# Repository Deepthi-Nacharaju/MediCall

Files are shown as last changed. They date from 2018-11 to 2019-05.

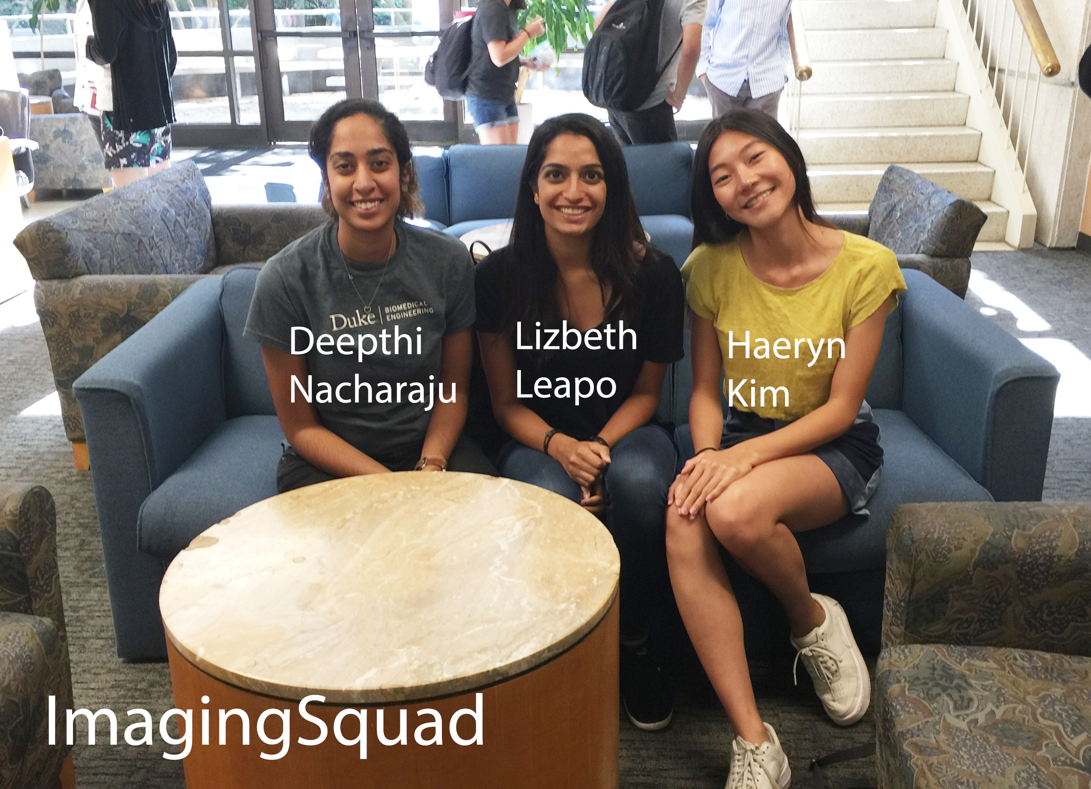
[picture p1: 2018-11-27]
Fall18/General/590TeamNames.jpg

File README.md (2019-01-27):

# MediCall

## Directory of Repository

| Subject                                 | Folder            | File Name                                                                      | Objectives      |
|-----------------------------------------|-------------------|--------------------------------------------------------------------------------|-----------------|
| Project Organization Strategies         | General           | ProjectOrganization.pdf                                                        |                 |
| Old Design Foundations Document         | Cycle_One         | 10_11_18 Design Foundations Document (DFD).docx                                |                 |
| Medical Device Development Worksheet    | Cycle_One         | HaerynLizDeepthi_Medical Device Development Worksheet 2018.xlsx                |                 |
| Updated Design Foundation Document      | Cycle_Two         | Updated Design Foundations Document (DFD).pdf                                                               |                 |
| Updated Spec Sheet PDF                  | Cycle_Two         | HOQ and Specs.pdf                                                              |                 |
| Cycle 2 Presentation                    | Presentations     | Final_Presentation.pptx                                                        |                 |
| Functional Decompositions               | Cycle_Two         | FunctionalDecomposition.pdf                                                    | Objective 1     |
| Pugh Matrix for Patient Alert Mechanism | Cycle_Two         | Scoring_User_Alert.xlsx                                                        | Objective 2     |
| Pugh Matrix for Nurse Alert Mechanism   | Cycle_Two         | Scoring_Alert.xlsx                                                             | Objective 3     |
| Pugh Matrix for Sensing Mechanism       | Cycle_Two         | Scoring_Sensor.xlsx                                                            | Objective 4     |
| +/- List for Battery v. Wall Power      | Cycle_Two         | BatteryvsMains.xlsx                                                            | Objective 5     |
| Pugh Matrix for Battery Type            | Cycle_Two         | Scoring_Battery.xlsx                                                           |                 |
| Hospital Policy on Bluetooth and Wifi   | Cycle_Two         | Bluetooth vs. Wifi Regulation Research.pdf                                     | Objective 6     |
| Sketch of System                        | Cycle_Two         | sketchofsystem.pdf                                                             | Objective 7     |
| Mechanical CAD of System                | Mechanical        | sensor.SLDPRT; sensor holder.SLDPRT; clamp.SLDPRT; strokesensorassembly.SLDASM | Objective 7     |
| Software Code Block Diagram             | Cycle_Two         | codeblockdiagram.pdf                                                           | Objective 8     |
| Demo Video of Prototype                 | Data              | IMG_7550.MOV                                                                   | Objective 9, 10 |
| List of System Components               | General           | Materials .xlsx                                                                |                 |
| Patient Flow Chart                      | Problem Statement | Patient flow-chart.pdf                                                         |                 |
|Updated Design Foundations Documentation| Cycle_Two| Updated Design Foundations Documentation. pdf

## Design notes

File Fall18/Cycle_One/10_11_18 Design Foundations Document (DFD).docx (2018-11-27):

MediCall: Design Foundations Document (DFD)

__________________________

Deepthi Nacharaju, Lizbeth Leapo, Haeryn Kim

Section 1: Design Context Review

In the United States alone, there are almost 36 million inpatient hospitalizations per year¹ with an average stay of 4.5 days². Many conditions can account for this staggering number of days spent in the hospital. The most common reason for this hospitalization is pregnancy, or neonatal in nature¹. In the ages of 65+, these reasons include heart disease, osteoarthritis, and back problems, the latter two of which can have a large impact on a patient’s mobility¹. As Americans spend increasingly large periods of time in hospitals, there should be an effort to make these stays as comfortable as possible.

During a time that can be scary, isolating, and stressful, people look to others for support and company. Though hospitals generally have visiting hours for family and friends to come see a patient, people often find themselves alone in their rooms. While patients are in inpatient care, they frequently need to call a nurse for help to use the restroom, eat, shift in their bed, and ask for medication. Rooms are usually set up with a call system, that can include a call bell, that enables the patient to alert their caregivers that help is needed. Beyond this, accessibility to reliable and efficient call bells reduces anxiety in the patient and increases family satisfaction with the stay³. Families are much more at ease leaving their loved ones in the hospital when they know a nurse is available nearby. Quick response times have even been shown to reduce fall risk and the incidence of pressure ulcers³. Nurses can help patients move from their bed to a chair and even the bathroom. Patients are also able to alert someone when they are uncomfortable from lying in the same position for too long. These are all important reasons why this line of communication is vital to a patient’s well-being.

There exist statewide regulations for the requirement of call bell or communication systems at nursing stations. For example, North Carolina has the following extensive requirement:

“In general patient areas, each room shall be served by at least one calling station and each bed shall be provided with a call button[...] Calls shall register with the floor staff and shall activate a visible signal in the corridor at the patient's or resident's door[...]A nurses' call emergency button shall be provided for patients' and residents' use at each patient and resident toilet, bath, and shower”⁴

The regulations go on to outline the number of call buttons required in rooms with multiple beds or bed stations, and even light indicators at corridor intersections. Other states, such as the state of Michigan, has no regulations regarding physical parameters of nursing stations⁴. In order for a solution to have potential market applications in the entire country, it must meet the most stringent of regulations, and in this case, encompass indicator lights and emergency buttons as well.

One study found the average number of calls placed by a patient to the nursing station to be 12 per day, with an increase in frequency around meal times⁵, perhaps to request help with trips to the restroom, or to ask for more food. Multiplying this value with the number of patients in a given unit – nurses receive 100 calls a day. With this high rate, the call bell must be reliable while also not cluttering the to-do list of nurses. A common complaint of the nurses in the study was that the high frequency of calls was disruptive to their busy shifts. Assessments, treatments, and teaching were now littered with patient calls⁵. There is a delicate balance between addressing immediate patient needs and tending to a longer term treatment plan composed of blood tests and imaging orders. Despite this, average response time was just 11 seconds⁵. This demonstrates that competing communication systems should be extremely efficient in transferring patient input, but also not be overly confusing, obtrusive, or disordered.

Current technologies include touch screens, hand held remotes, and pancake sensors for patients to create a user input. This signal is then translated to either a centralized screen at the nurses station, or a particular medical personnel’s handheld device³. Some systems even include a verbal system in which the patient indicates their specific need, and the receiver determines if the call should be routed to a registered nurse or to a nurse’s assistant⁴. Instead of just a generic call bell, some systems also indicate the specific need, and allow the user to choose from several common call requests. The patient lets the nurse know they need to use the restroom, change the channel, or shift their position remotely. What these systems typically seem to lack is feedback from the unit to the user that the call mechanism has been triggered. Because alertness or cognition in these patients, especially neurological patients, can be diminished, this feedback is vital to ensure that a purposeful call has been triggered or than an accidental one has not been placed. On the other hand, some sensors are too easily triggered, calling for nurses when the patient was merely shifting in their bed. This leads to further frustration, and nurses and patients often throw the call system aside altogether.

Physical sensors like these are often limited to use by patients with full mobility and dexterity in their hands. The systems that require verbal input are limited to those who can speak loudly and clearly. Finding a suitable system for patient populations with limited speech or physical capabilities remains a challenge.

Patients in the Neurocritical Care Unit of the Duke Medicine Pavilion, or DMP, suffer from a wide range of ailments that vary in severity and also vary the length of each stay. Frequently, patients have suffered from strokes, resulting in paralysis that ranges from monoplegia to quadriplegia⁶. Some patients have considerable dexterity in their upper extremities, while others are completely paralyzed and can barely speak or see. Loss of function in the arms and legs can be especially dangerous because the patient is not able to catch his or her falls, rotate to ease pain from lying on their backs for long periods of time, or move to the restroom. Paralysis can also result from other neurological diseases, including physical trauma, neuropathy, and Parkinson’s Disease. The loss of any important functions limits accessibility to remotes with several buttons, or verbal cues.

Similar limitations can be found in other clinical populations, including young people suffering from orthopedic injury, and middle-aged patients battling cancer. This creates a larger context for the relevance of this issue. Outside of neurological units, loss of motor skills can be prevalent in oncology, trauma, and cardiac centers across the country. Any patient that is admitted to the hospital, could potentially find him or herself too weak or entirely unable to lift their arms, while simultaneously at need of frequent attention and care. In any combination, these limitations can be extremely detrimental in calling for help and could result in increased risk of death or serious injury.

At the Duke Medicine Pavilion, there are several adapted call bells in place, three of which are pictured below in Figure 1⁷. These include the standard call bell with a button on the patient’s TV remote, a handheld push-button call bell, and a pancake call bell. The push-button and pancake call bell are used for patients with a larger degree of physical or cognitive impairment.

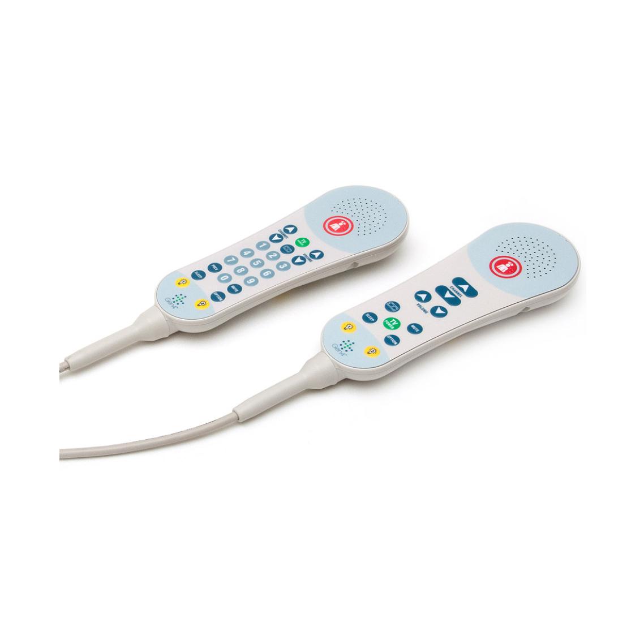
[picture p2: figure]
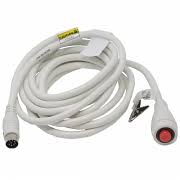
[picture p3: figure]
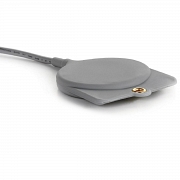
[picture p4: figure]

Figure 1. Call bells implemented in the Duke Medicine Pavilion. From left to right, the standard TV remote call bell, the handheld push-button call bell, and the pancake call bell¹³.

After observing the use of these devices in the Neurocritical Care Unit of the DMP, it became evident that while there are adapted call bells for patients with specific physical or cognitive needs, several factors still result in faulty patient-to-nurse communication. The standard call bell is designed for patients with very few physical or cognitive limitations. However, this bell is also often provided to patients with visual impairments who struggle to differentiate the call bell button from the TV remote buttons. Nurses sometimes attach ECG leads to the call bell button on the remote to make it easier for those patients to use the call bell function. The push-button call bell works well for patients with a relatively high degree of hand dexterity, but the button has no stand, and often gets dropped on the floor or lost in the hospital bedding. The button also has no feedback mechanism to alert the patient that it has been activated. This generally leads to a high number of false pages to the nurses’ station. The pancake sensor has a similar problem. It is designed for patients with very limited hand dexterity. However, it is extremely sensitive and does not have a feedback mechanism. According to Kim Powell, a speech pathologist who works in the Neurocritical Care Unit, the pancake sensor is far too sensitive to be used effectively and it results in the largest amount of false alerts.

Each call bell in a patient room, regardless of the type of call bell, is connected first to a station on the patient’s ECG cart, and then to a wall power supply. One of the largest failures of the call bell system at the DMP is the lack of attention in plugging in both of these connections. This also dramatically reduces patients’ accessibility to nurses when in need.

It is critical that patients are able to contact nurses when they are in need of assistance. Patients with limited hand dexterity find both standard and adapted call bells at Duke to be particularly unhelpful. The systems are either physically inaccessible, unplugged, or too sensitive. The ultimate challenge is addressing all of these inconveniences with one device or system.

Our primary need is to find a way to address inadequate patient-to-nurse communication in patients with limited hand mobility that increases accessibility to nurse assistance while reducing the number of false alerts caused by current call bell systems.

Section 2: Market Analysis

In the context of this problem, there were two ways to segment the available market. The first was according to medical unit or service provider the patient would seek out to receive care. The market includes smaller segments such as palliative care units, surgical in-patient clinics, and at home care.

The target segments of focus include Nursing and Retirement homes with a predicted total addressable market (TAM) of $42,228,000⁸,⁹ and Neurocritical Care Units (NCUs) with a TAM of $262,800¹⁰,¹¹. The primary criteria used to determine the target segment includes a target population that experiences limited mobility of their upper extremities, with potential limitations in speech, sight, and cognition.

Care systems for the elderly regularly take care of people at the end of their life. In this stage, people experience declines in both physical and mental health, demonstrated by decreases in balance, dexterity, muscle strength, and mental sharpness. These people would also experience potential challenges with using traditional call bell systems. In the United States, the entire population of nursing and retirement homes includes 15,600 Nursing homes with 1.7 million beds⁹. This translates to about 109 beds per facility and a need for an equivalent number of call bells. In order to determine their willingness to pay, competitive products were analyzed for cost per unit.

Competitive products can be found in Table 1, below. Each system was broken down into per patient room costs. For example, a system that cost $1,000, but supplied 10 individual modules, was translated to a $100/bed cost. On average, the cost per bed was $150. To calculate predicted Total Addressable Market (TAM), the number of estimate beds per segment in the US was multiplied by the cost per bed. For the Nursing/Retirement home segment, there are estimated number of 15,640 homes with an average of 108 beds. The total of 1,689,120 beds was multiplied by $150/bed for a TAM of $42,228,000⁸,⁹.

NCUs also care for a patient population with physical and mental limitations. NCUs typically treat acute ischemic strokes, cases of meningitis, traumatic brain injury and cerebral aneurysms, along with a host of other potentially fatal conditions. Patients experience varying levels of consciousness and frequently need to alert a nurse when they are awake. However, with this level of brain injury, many patients experience spastic or disjointed movements of their extremities. Across the country there are 73 of these units¹⁰. Similar conditions can be also found in Neurology units, which are found more frequently in hospitals. Estimating the number of beds per unit to be around 24, coming from the number of beds in Duke University’s Neurological ICU⁹, to total number of beds in the US as 1,752. Again, multiplying cost per bed equates to $262,800¹⁰,¹¹.

To further narrow down the target population, these segments were refined by considering the physiological limitations of the patients. This is the second way in which this market could be segmented. In general, there are three overarching themes to what created challenges while trying to utilize the traditional call-bell system, both in the larger scope of disabilities and in the Duke Medical Pavilion Neuro ICU client. These themes include cognitive impairments, when the patient lacks awareness or alertness to understand how a traditional button system works. The patients could also experience sensory loss, in which blindness prevents them from seeing the difference between various buttons on a remote. Another limitation is more physical in nature, where either paralysis or jerky movements have trouble exhibiting the dexterity needed for traditional call-bell systems.

After thorough market analysis, the primary target market segment will be those experiencing challenges with the mobility of upper extremities in Nursing/Retirement homes and Neurocritical Care Units, with potential for extension into other segments given success with this group.

Section 3: Identifying Customer Needs

Kim Powell is a clinical expert at the cross section of healthcare and communication, and a speech pathologist in the Neuroscience Department at Duke Hospital. She specializes in stroke recovery, and many of the devices in her unit are tailored to patients with limited hand dexterity, poor cognitive ability, or paralysis. Ms. Powell expressed the limitations of the sensitive adaptive devices such as the push-button and pancake call bells. She conveyed frustration with the wiring of the current call bell system and facilitated an introduction to a stroke patient who provided insight into image comprehension limitations post-stroke.

Observations during the shadowing visit led to the conclusion that the call-bells in the unit were either too sensitive and sent false alerts to nurses, or that they were entirely unused because they were either unplugged or physically inaccessible to the patient. There was a need to reduce the amount of excessive wiring attached to the call bell, so that it was accessible when needed, but not in the way otherwise. Patients with cognitive limitations also need a clear indication that the call-bell is activated, because the current devices do not provide any mode of feedback. The full list of customer needs is provided in Table 1 below.

Table 1. Identified Customer Needs

No. | Type of Need | Need | Priority
1 | Patient | Device is easily accessible for patients with limited hand dexterity | 1
2 | Patient | Device provides some mode of feedback when activated | 2
3 | Patient | Device will not be in the way when not in use | 3
4 | Nurse | Device transmits the signal to multiple receivers | 2
5 | Nurse | Device quickly transmits the signal to nurses | 2
6 | Nurse | Device reduces the amount of false alerts going to the nurses' station | 2
7 | Nurse | Device is durable and can withstand accidents | 5
8 | Nurse | Device reduces excessive wiring | 2
9 | Payer | Device has similar cost to other competitive nurse call systems | 4
10 | Payer | Device can be produced and purchased in bulk so hospitals can use in each patient room | 5
11 | Regulatory | Device complies with nursing units regulations set by NC | 2
12 | Regulatory | Device does not cause any adverse health effects, or pose a trip or fall hazard to the patients | 3
13 | Regulatory | Software on the device should meet IEC Medical Device Software Standards | 5

The customer needs are organized into patient needs, nurse needs, payer needs, and regulatory needs. This device has two primary users: the patient and the nurse. The patient needs deal with accessibility and use of device, while the nurse needs deal with the transmission and reliability of the alert in itself. The payer, Duke Hospital, needs this device to have a similar cost to competitive call systems. In terms of regulatory standards, the call system must comply with software and safety regulations met by the Duke Medicine Pavilion.

In establishing a hierarchy for our customer needs, increasing patients’ accessibility to nurses is a higher priority than reducing the amount of false alerts sent to nurses. The risk of a patient unable to get medical attention supersedes the inconvenience of a false alert. It is also important that the device provides some sort of feedback, which allows for easier use by patients with cognitive limitations, and subsequently reduces the amount of false alerts because it prevents repetitive pushing. Meeting state regulations for nursing units is also critical to ensure potential usage of our device in hospital rooms. Long-range and fast signal transmission was prioritized over durability, because an effective and fast alert is most beneficial to the patient and nurse. Reducing the amount of wires is a medium priority, because it is more of an inconvenience than a significant risk. Cost-efficiency and meeting software standards were of lowest priority because we first want to establish an effective and reliable device.

Section 4: Design Specifications

In order to reliably quantify the accuracy with which our product serves the customer needs, the following design specifications were determined to serve as quantitative judgment criteria.

Table 2. Target Specifications

Spec. No. | Need Nos. | Specification | Units | Competitive Value | Marginal Value | Ideal Value
1 | 3, 8, 12 | Wires from device to power | Number | 1-2 | 1 | 0 (wireless)
2 | 1, 2, 11 | Modes of button feedback (buzzing/light/sound) | List | 0 | 2 | 3
3 | 4 | Signal transmission range | m | 150 | 200 | 300
4 | 8 | Battery life | months | 0 (connected to wall power) | 2-3 | 6
5 | 7 | Water resistance | Standard | IPX5 | IPX4 | IPX5
6 | 1 | Weight of device | g | 110 | 100 | 50
7 | 9, 10 | Cost of device | $ | 150 | 100 | 70

The units include simple tallies (denoted as ‘numbers’), statistical values obtained through trials (in percentage), and categorization by standards. Standard pertains specifically to the requirements for water resistant devices as defined by the IP code, provided in the International Electrotechnical Commission (IEC) standard 60529¹². Whereas the search for comparable products did not provide their IP levels, we could narrow down the desired liquid ingress protection for our product. IPX5 means the device would be protected from a low level stream of water at any angle¹².

These criteria were determined by brainstorming the metrics associated with specific customer needs.To ensure that patients or nurses can easily access our product we wanted to make sure that it was easy to find and within reach, which is measured by the time it takes to find and activate the device. Current technologies at the DMP currently do not have feedback mechanisms, so a quantitative measure of types of feedback such as vibration, light, and sound was added as a specification. This specification also addresses the state regulation requiring a visible signal for nursing call units⁴. To address excessive wiring, the number of connections the device has to a wall plug or a source of power is a major specification. Some specifications were necessary to cover the basic functions of a call bell such as notifying the nurses within a reasonable range. The only customer need that was not matched by these quantitative specifications was the software regulation need (13), because this would require a qualitative check of the software.

Furthermore, we researched comparable products on the market and their design specifications to complement our specifications, as well as competitive values. For instance, the competitive value of cost was an averaged price projected on the nurse call products catalog of healthcare facilities companies¹³. Competitive values of weight were similarly found from comparable call bell products detailed in the market analysis. Competitive values for false alert rates were found in literature on alarm fatigue¹⁴. Ideal values were subjectively determined as the best possible values, without considering any scope or limitations of the project. Marginal values were determined as mid-range values between the competitive and ideal. For instance, whereas most systems were comprised of a base station dependent on wall plugs and pagers running on batteries with more than 6 months of battery life, 2-3 months of peak operation time were deemed as reasonable for our standalone, wireless communication device. Ideally, the device would be wireless with long battery life, water resistant, cheap, accessible in less than a minute, and have multiple modes of feedback.

Citations

[1] McDermott, K. W., Elixhauser, A., & Sun, R. (2017). Trends in Hospital Inpatient Stays in the United States, 2005-2014. Healthcare Cost and Utilization Project. https://www.hcup-us.ahrq.gov/reports/statbriefs/sb225-Inpatient-US-Stays-Trends.jsp

[2] Weiss, A. J., & Elixhauser, A. (2014). Overview of Hospital Stays in the United States, 2012. From Healthcare Cost and Utilization Project. https://www.hcup-us.ahrq.gov/reports/statbriefs/sb180-Hospitalizations-United-States-2012.pdf

[3] Galinato, J., Montie, M., Patak, L., & Titler, M. (2015). Perspectives of Nurses and Patients on Call Light Technology. Computers, Informatics, Nursing : CIN, 33(8), 359–367. http://doi.org/10.1097/CIN.0000000000000177

[4] Statewide Regulations for Nursing Units. (2011). Health Policy and Management. http://www.hpm.umn.edu/nhregsplus/NH%20Regs%20by%20Topic/NH%20Regs%20Topic%20Pdfs/PE%20-%20Nursing%20Unit/category_pe_nursing%20unit%20state%20regulations.pdf

[5] Roszell, S., Cheryl B. Jones, & Lynn, M. R. (2009). Call Bell Requests, Call Bell Response Time, and Patient Satisfaction. Journal of Nursing Care Quality, 24(1), 69-75. doi:10.1097/01.NCQ.0000342938.99036.9f

[6] Divani, A. A., Majidi, S., & Barrett, A. M. (2011). Consequences of Stroke in Community-Dwelling Elderly: The Health and Retirement Study 1998-2008. Stroke., 42(7), 1821-1825. doi:10.1161/STROKEAHA.110.607630

[7] Nurse Call. Medline. Retrieved from https://www.medline.com/category/Nurse-Call/Z05-CA15_12_02_07

[8] Smart Caregiver Two Call Buttons & Wireless Caregiver Pager. https://www.amazon.com/Smart-Caregiver-Buttons-Wireless-Pager/dp/B0032FMSWS

[9] Nursing Home Care. (2014). From Centers of Disease Control and Prevention. https://www.cdc.gov/nchs/fastats/nursing-home-care.htm

[10] Ward, M., Shutter, L., Branas, C., Adeoye, O., & Carr, B. (2012). Geographic access to US Neurocritical Care Units registered with the Neurocritical Care Society. Neurocritical Care, 16(2), 232-240. doi:10.1007/s12028-011-9644-2.

[11] Neurocritical Care Unit, Duke Medical Pavilion, 8E. Department of Neurology- Duke University School of Medicine. https://neurology.duke.edu/divisions/critical-care-and-vascular-neurology/neurocritical-care-unit-duke-medical-pavilion-8e

[12] International Electrotechnical Commission. (2013). Degrees of protection provided by enclosures (IP Code) (Standard No. 60529). Retrieved from https://subscriptions.techstreet.com/products/653435

[13] Curbell Medical. (2017). ‘Nurse Call and Healthcare Bed Accessories.’ Retrieved from https://curbellmedical.com/wp-content/uploads/pdfs/nurse_call/map466d_curbell_nurse_call_and_bed_products_catalog.pdf

[14] Jones, K. (2014). Alarm fatigue a top patient safety hazard. CMAJ- JAMC, 186(3), 178. doi: 10.1503/cmaj.109-4696

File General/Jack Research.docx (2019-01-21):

http://www.circuitbasics.com/how-to-hack-a-headphone-jack/

standard ¼” phone plug for single push button ^

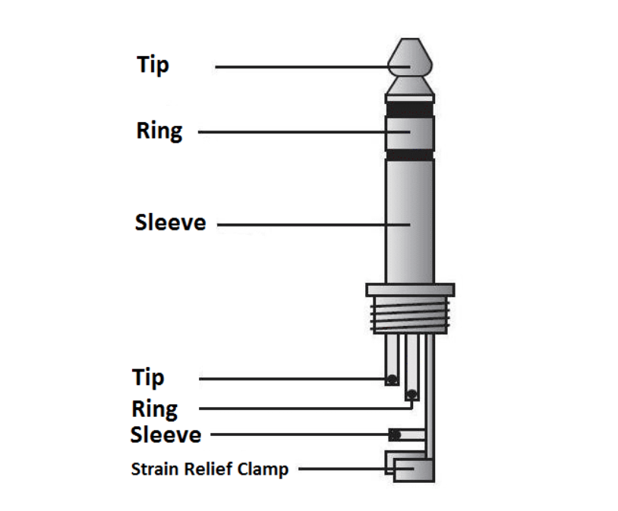
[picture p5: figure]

Tip = Power

Ring = Signal

Sleeve = Ground

1/21/19

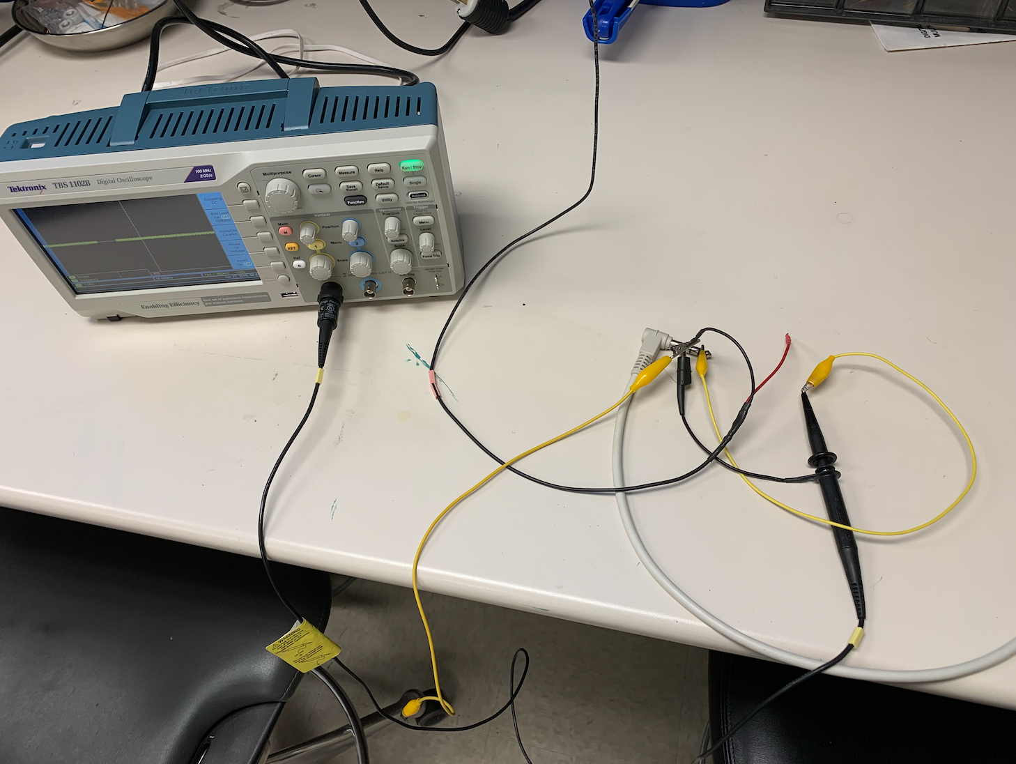
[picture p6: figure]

Deepthi: Used oscilloscope to probe both tip and ring with power on the other (5V). Saw signal when pushing the button but the power supply was maxing out a 1.5A. When power was on the ring, power supply was constantly maxed out; when power was on the tip, the power supply dropped down to 0A until the button was pushed (then it maxed out). Does the external circuit need a current limiting resistor….?

Further Questions:

Do we need to current limit the incoming signal?

How high and for how long does the voltage signal need to read high to trigger the wall system?

How does the nurse shut off the call?

What is the lag time between pushes for separate calls?

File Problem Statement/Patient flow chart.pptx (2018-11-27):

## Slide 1

Evidence of patella fracture? i.e. X-ray

Ambulatory care: initial diagnosis, treatment, rehabilitation

Patient has acute pain in the knee, and difficulty walking i.e. unable to lift foot

Displaced bones?

No

Apply cast or splint.

Closed fracture?

Have abrasions healed?

Surgical procedure

Pain management and rehab

No

No

Open fracture?

Ambulatory care: follow-up care

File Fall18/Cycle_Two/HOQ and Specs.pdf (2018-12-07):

### House of Quality, Functional Specs

Spec #1 | Spec #2 | Spec #3 | Spec #4 | Spec #5 | Spec #6 | Spec #7

Priority

CUSTOMER REQUIREMENTS/NEEDS

Time it takes to find and | Percentage of false positives | Number of connections from device to power | Number of different settings/ modes to adapt to varying hand dexterities | Battery life | Water resistance | Cost of device
1 | Easily accessible for patients with limited mobility | X | | | X
2 | Should be understood by patients with limited cognitive ability | | | | X
3 | Reduce the amount of false-positives going to the nurse's station | | X
4 | Reduces excessive wiring | | | X | | X
5 | Transmit the signal to multiple receivers
6 | Durable and can withstand accidents (ex. water spray) | | | | | | X
7 | Able to be produced/purchased at competitve cost | | | | | | | X
| | 1-2 min (2) | 85% (1) | 1-2 (Current system at Duke requires two connections to wall reach wall power) | 1 (per adapted call bell device) (3) | 0- Needs wall-power | IPX5 | $150 (from comparative chart on Market Analysis tab)

Competive Values
Marginal Value | 1 min | 20% | 1 | 2 | 2-3 months | IPX4 | $100
Ideal Value | 0.5 min | 5% | 0- wireless | 4 (one device for various types of mobility) | 6 months | IPX5 | $70

Sources:
1. https://www.ncbi.nlm.nih.gov/pmc/articles/PMC3928208/
2. https://www.frequencyprecision.com/products/touch-sensitive-button-pager-linked?variant=6167456003
3. https://curbellmedical.com/specialty-call-cords/
4. https://www.amazon.com/Housecare-Caregiver-Caregivers-Waterproof-Transmitters/dp/B07DHTVBH1/ref=sr_1_4?ie=UTF8&qid=1539227293&sr=8-4&keywords=nurse+call+system+for+hospital

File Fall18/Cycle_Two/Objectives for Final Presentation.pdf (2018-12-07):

| | Objectives for Cycle 2
| Related Specifications | | (< 300) | Graded Points
| Brainstorming Objectives
1 | Number of different settings/ modes to adapt to varying hand dexterities; Number of connections from device to power, Time it takes to find and use | Outline a functional decomposition of device | 150
2 | Time it takes to find and use | Pugh Matrix to isolate 2 ways device could potentially alert the user that the call-bell was activated | 150
3 | Time it takes to find and use | Pugh Matrix to isolate 2 ways device could alert the nurse that the call-bell was activated | 150
4 | Time it takes to find and use, Number of different settings/ modes to adapt to varying hand dexterities | Pugh matrix to decide between voice activation, foot pedal, IR sensor, or button. | 200
5 | Battery life | Create list of pros and cons for both a battery supply and a main voltage supply and decide on suitable option | 150
6 | Transmission Range | Research Duke Hospital policy on Bluetooth/WiFi in patient rooms | 100
| Prototyping Objectives
7 | Number of different settings/ modes to adapt to varying hand dexterities, Weight of device | Detailed sketch of all components of sensor and bedside stand/attachment | 200
8 | Signal transmission | Draw a code block diagram | 200
9 Number of different settings/ modes to | adapt to varying hand dexterities | After choosing mechanism in Objective 5, low fidelity prototype mechanism for voice activation, button, or IR sensor. | 350
10 | Signal transmission | Configure wireless connection (e.g. Particle board or Bluetooth serial module) with at least one remote signal receiver | 350
| | TOTALS (= 2000) | 2000

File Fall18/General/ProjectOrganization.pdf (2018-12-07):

## MediCall

Project Organization Strategies
Haeryn Kim
Lizbeth Leapo
Deepthi Nacharaju

To work collaboratively on live documents, we initially used Google Drive to house all word documents and excel sheets. As these documents became fixed, we switched to another mode of project management. Now, all project material, including videos, PDFs, and sketches, are tracked via GitHub. All milestones, objectives, and their associated progress are organized with the project feature on GitHub using a Kanban board.

The MediCall folder is split into Cycle One, Cycle Two, Data, General, Mechanical, Presentations, and Problem Statement folders. All previous versions have been committed and can be found in the Git history.

https://github.com/Deepthi-Nacharaju/MediCall

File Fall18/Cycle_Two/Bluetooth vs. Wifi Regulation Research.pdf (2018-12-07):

Bluetooth vs. Wifi Regulation Research
Haeryn Kim, Lizbeth Leapo, and Deepthi Nacharaju

What is considered Protected Health Information?
According to the HIPAA Administrative Simplification regulations by the U.S. Department of Health and Human Services, the term health information refers to “any information, including genetic information, whether oral or recorded in any form or medium, that: (1) Is created or received by a health care provider, health plan, public health authority, employer, life insurer, school or university, or health care clearinghouse; and (2) Relates to the past, present, or future physical or mental health or condition of an individual; the provision of health care to an individual; or the past, present, or future payment for the provision of health care to an individual.” Protected health information, on one hand, means “individually identifiable health information that is: (i) Transmitted by electronic media; (ii) Maintained in electronic media; or (iii) Transmitted or maintained in any other form or medium.” (HIPAA Simplification)

What are areas of protected health information that is relevant to our product that the hospital currently reserves the right to use or disclose, under patient consent?
The hospital currently can use protected health information for healthcare operations, which include “reviewing and improving the quality, efficiency and cost of care that we provide to you and other patients.” (Duke Health, Notice of Privacy Practices)

What are the current privacy practices at Duke University Hospital?
On Duke University Health System websites, they use analytics tools and other third party technologies, such as Google Analytics or DoubleClick Cookies to collect non-individual information in the form of various usage and user metrics when the user employs these services. The mentioned information include “cookies, IP addresses, device and software identifiers, referring and exit URLs, onsite behavior and usage information, feature use metrics and statistics, usage and purchase history, MAC Address, mobile unique device ID, geo-location, demographic and interest data, and other similar information.” (Duke Health, Website Privacy Policy)

They also use a WiFi network as is secured under settings required by the Code of Federal Regulations (CFR) Title 45, Part 164, Subpart C. The CFR splits the requirements into three categories: administrative (pertaining to the configuration of the wireless LAN), physical (ex. security-lock secured access points), and technical (separation of traffic, WPA2 and PSK encryption). Should our device transmit information using WiFi, encryption should be taken care of by the hospital’s system; but multiple devices use the same WiFi network at the hospital.

How is information transmitted in Bluetooth?
Bluetooth networking transmits data via low-power radio waves. It communicates on a frequency of 2.45 gigahertz. Bluetooth systems can create a personal-area network, or a piconet, that may fill a room, e.g. the patient room. Once a piconet is established, the connected devices randomly hop frequencies in unison (1600 hops/sec) so they stay in touch with one another and avoid other Bluetooth connections that may be operating in the same room. (Franklin and Layton)

What kind of individually identifiable data are generated by Bluetooth?
In the case of our system, the signal detector (the bedside sensor) that detects patient input, that reads and transmits boolean data (True if a patient’s hand is near the sensor for more than five seconds) to a signal receiver (a servo motor) unit that is in the same room, within the range of Bluetooth. This data is not individually identifiable of the patient.

How is information transmitted in Wifi?
Data is transmitted over Wifi using the connection to the internet. Usually, there is a central node (a router) that acts as the interface between wired and wireless connections and manages communication between devices. This device also exchanges data packets between devices. It is called an Access Point (AP) or a router. A client, a mobile phone, laptop or workstation computer, connects to the AP. The client sends data packages to a router that is modulated using Orthogonal Frequency Division Modulation. These data packages are tagged with the physical address of the receiving device (MAC address) and it is sent to the atmosphere of the Mac ID of receiver. All of the devices in the range of the AP can capture this package, but the only device with the specified Mac ID will be able to retrieve and process the data. (Syed)

What kind of individually identifiable data are generated by Wifi?
Similarly to Bluetooth, the data being transmitted is agnostic to the user so there is no individually identifiable data transmitted through Wifi between the devices. However, there necessarily will be information transmitted through the hospital Wifi and characteristic to any requests made through the internet, an exposed Mac/IP address of the devices. However, multiple devices require connection to the same network and it would be unlikely that our device can be configured to a separate network traffic. It would be also harder to troubleshoot security, since our developers would have limited access to any information pertaining the Duke Health WiFi configuration.

Could anything mentioned have possibility of being considered private patient record? No. The two devices that comprise our system will transmit signal from an IR sensor, that generates information agnostic to the user, to a signal receiver that does not either interface with Bluetooth or Wifi to interact with a remote controller button. This interaction is purely mechanical.

Why is Bluetooth more apt for our purposes?
In consideration of the attributes that are inherent in wireless connections, such as usability, power, distance, data rates, and coexistence, Bluetooth is the ideal option as a wireless connection module for the degree of performance necessary for our device. It consumes the least power of all of the networked technologies. It typically requires fractions of the power of IEEE 802.11b solutions. Typical PDA implementations yield 6–10 hours of usage compared with 2–4 hours for 802.11 solutions using the same batteries. (Saltzstein) With Bluetooth, no IP addressing is involved, so it is relatively quick and easy to set up small networks of devices. It also has the necessary security features to comply with HIPAA requirements for patient data. It is cableless ( a high priority in our design specifications matrix), has high connectivity within individual patient rooms, security that provides access control and software encryption options, is reliable based on resistance to ambient radio frequency noise, and has a low level of interference with other technologies.

References

Duke Health. Notice of Privacy Practices. https://www.dukehealth.org/privacy. Web. 2 Dec. 2018.

Duke Health. Website Privacy Policy. https://www.dukehealth.org/privacy. Web. 2 Dec. 2018. Franklin, Curt and Layton, Julia. How Bluetooth Works. https://electronics.howstuffworks.com/bluetooth2.htm. Web. 2 Dec. 2018.

The Health Insurance Portability and Accountability Act Administrative Simplification Part 164 Subpart C. Web. 4 Dec. 2018.

Public Welfare, 45 C.F.R. § 164.C (2012).

Saltzstein, William E. Bluetooth and Beyond: Wireless Options for Medical Devices. Medical Device and Diagnostic Industry. https://www.secplicity.org/2015/08/31/hipaa-compliant-wi-fi-what-you-need-to-know/. Web. 6 Dec 2018.

Syed, Amal. How does data get transmitted via Wifi? Quora. https://www.quora.com/How-does-data-get-transferred-via-WiFi. Web. 5 Dec. 2018.

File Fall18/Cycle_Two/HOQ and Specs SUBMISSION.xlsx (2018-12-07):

House of Quality, Functional Specs
 |  | Spec #1 | Spec #2 | Spec #3 | Spec #4 | Spec #5 | Spec #6 | Spec #7 | Spec #8
Priority | CUSTOMER REQUIREMENTS/NEEDS | Time it takes to find and use | Percentage of false positives | Number of connections from device to power | Number of different settings/ modes to adapt to varying hand dexterities | Transmission range | Battery life | Water resistance | Cost of device
1 | Easily accessible for patients with limited mobility | X |  |  | X
2 | Should be understood by patients with limited cognitive ability |  |  |  | X
3 | Reduce the amount of false-positives going to the nurse's station |  | X
4 | Reduces excessive wiring |  |  | X |  |  | X
5 | Transmit the signal to multiple receivers |  |  |  |  | X
6 | Durable and can withstand accidents (ex. water spray) |  |  |  |  |  |  | X
7 | Able to be produced/purchased at competitve cost |  |  |  |  |  |  |  | X
 | Competive Values | 1-2 min (2) | 85% (1) | 1-2 (Current system at Duke requires two connections to wall reach wall power) | 1 (per adapted call bell device) (3) | 152 m (4) | 0- Needs wall-power | IPX5 | $150 (from comparative chart on Market Analysis tab)
 | Marginal Value | 1 min | 20% | 1 | 2 | 200 m | 2-3 months | IPX4 | $100
 | Ideal Value | 0.5 min | 5% | 0- wireless | 4 (one device for various types of mobility) | 300 m | 6 months | IPX5 | $70
Sources:
1. https://www.ncbi.nlm.nih.gov/pmc/articles/PMC3928208/
2. https://www.frequencyprecision.com/products/touch-sensitive-button-pager-linked?variant=6167456003
3. https://curbellmedical.com/specialty-call-cords/
4. https://www.amazon.com/Housecare-Caregiver-Caregivers-Waterproof-Transmitters/dp/B07DHTVBH1

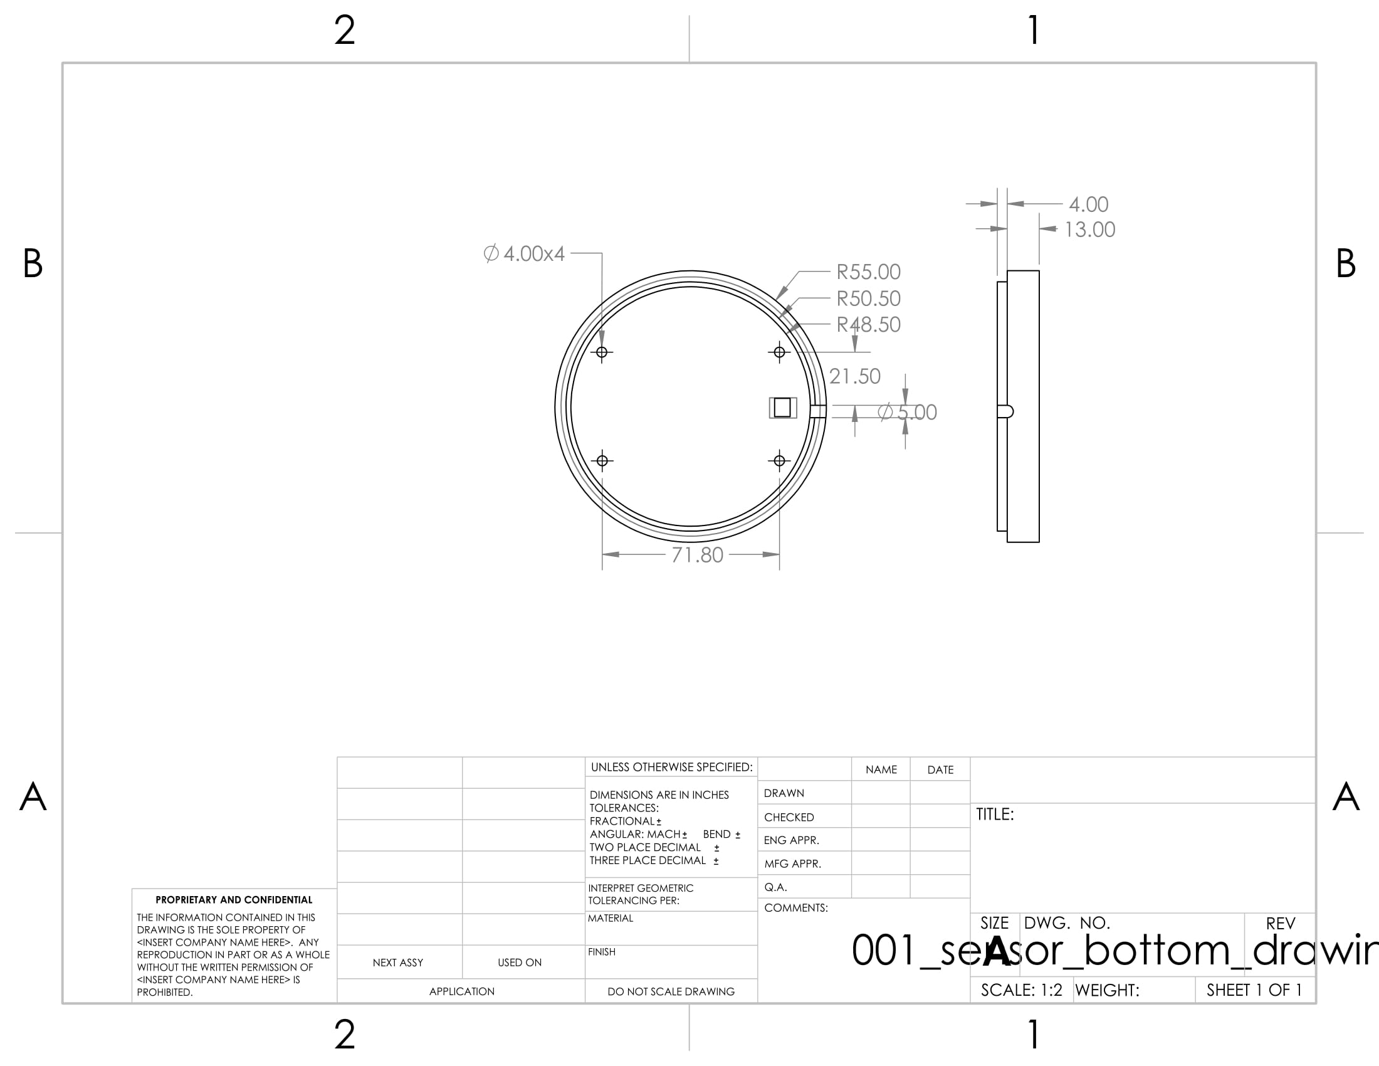
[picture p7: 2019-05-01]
Spring19/Mechanical/Drawings/001_sensor_bottom.jpg

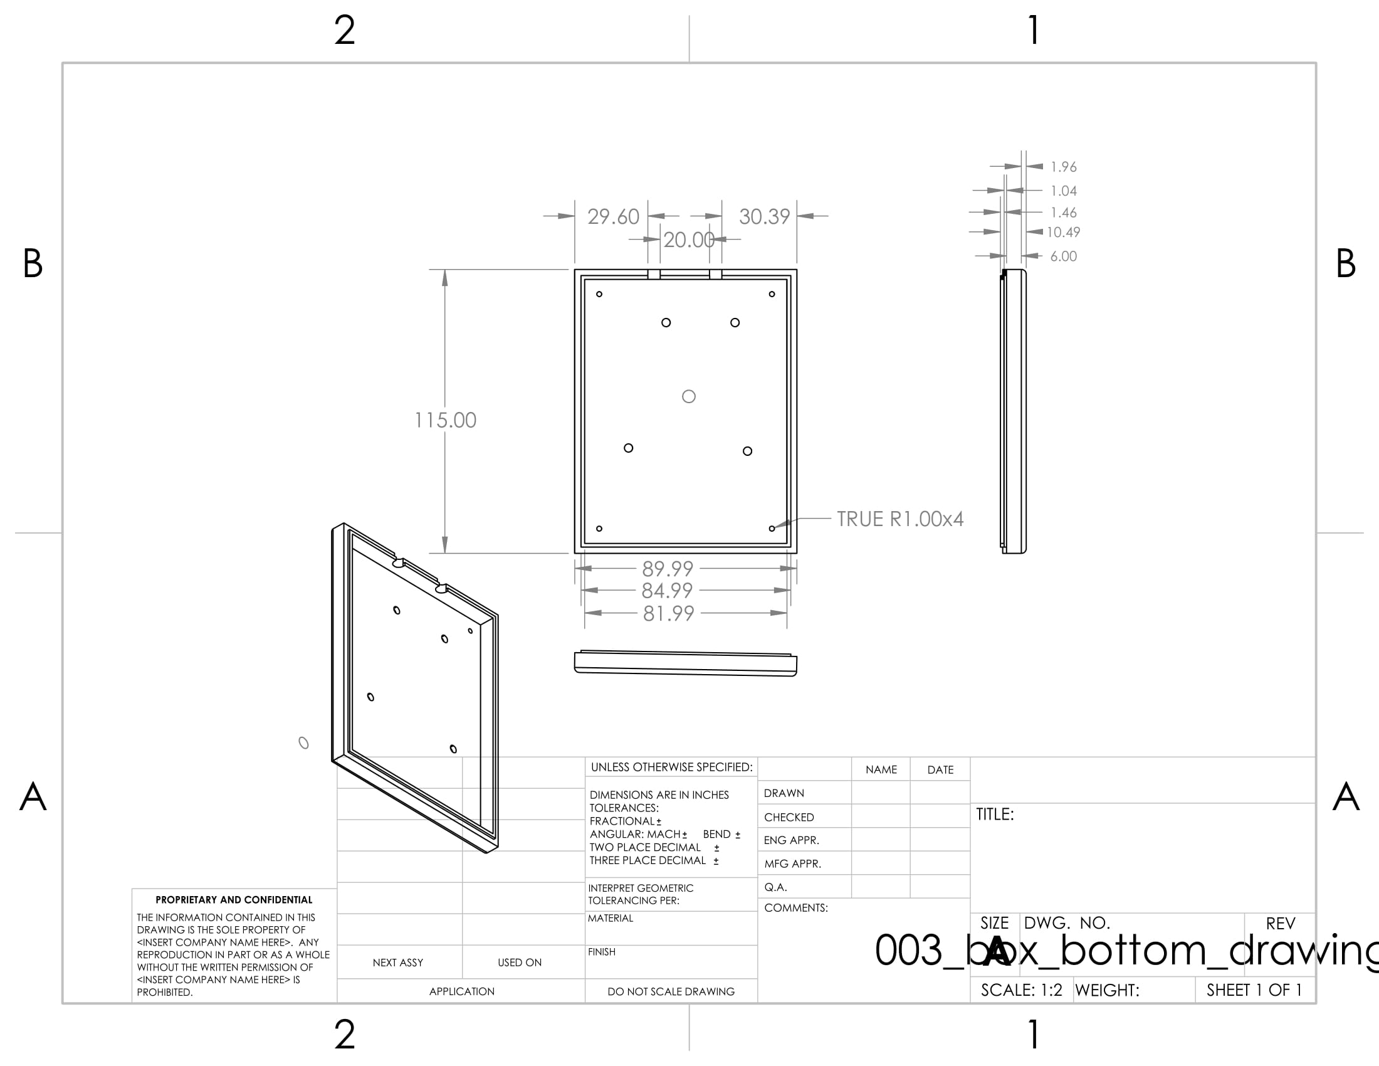
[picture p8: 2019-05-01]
Spring19/Mechanical/Drawings/003_box_bottom.jpg

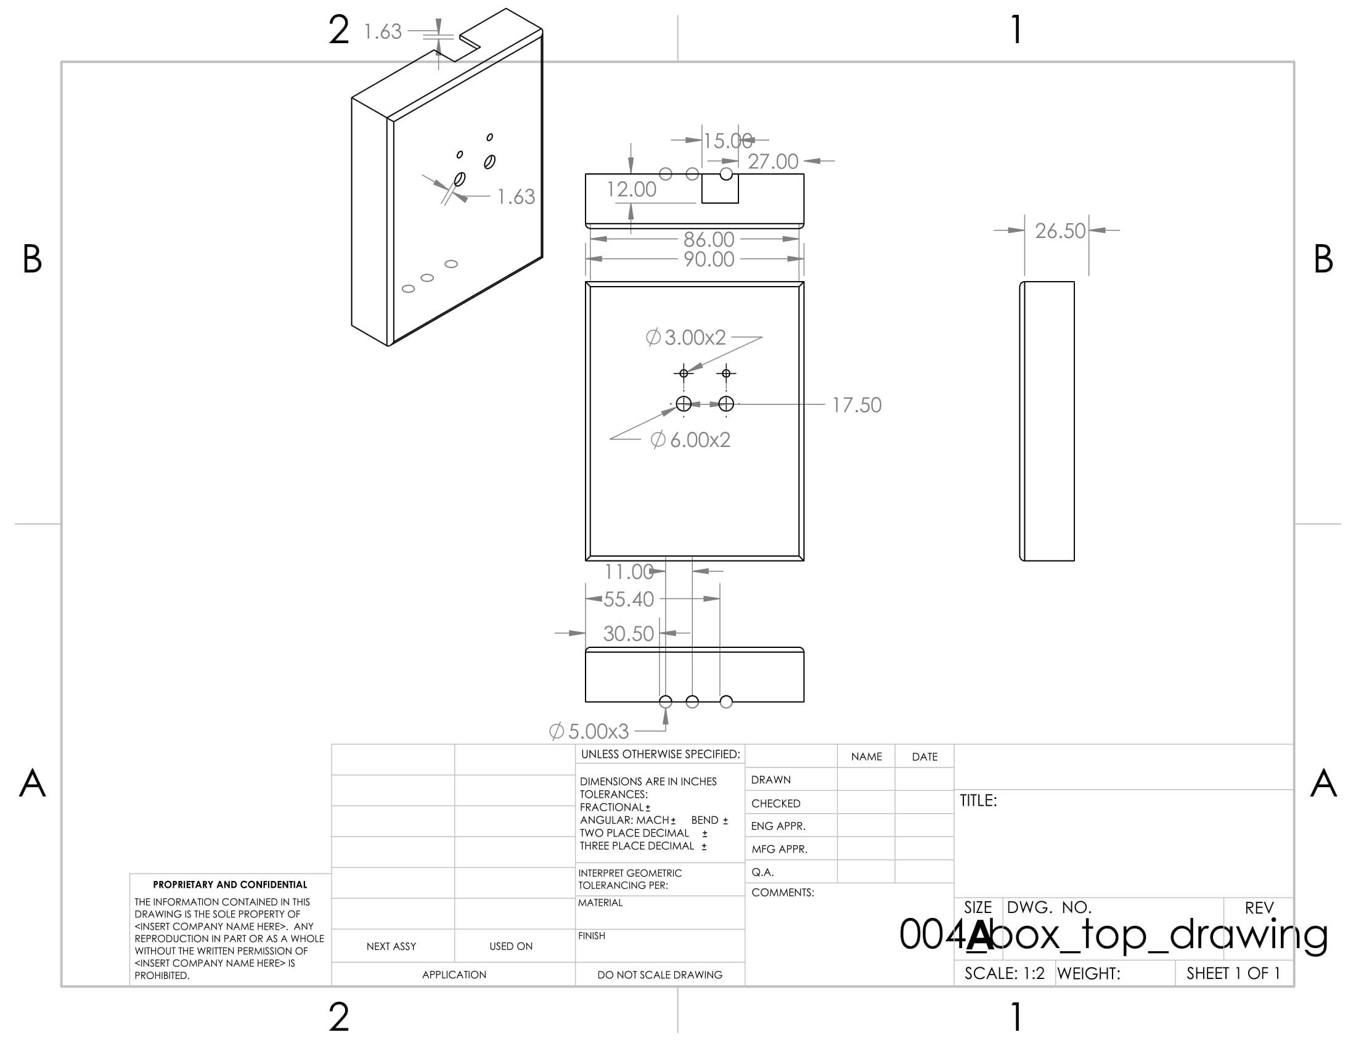
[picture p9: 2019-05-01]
Spring19/Mechanical/Drawings/004_box_top.jpg

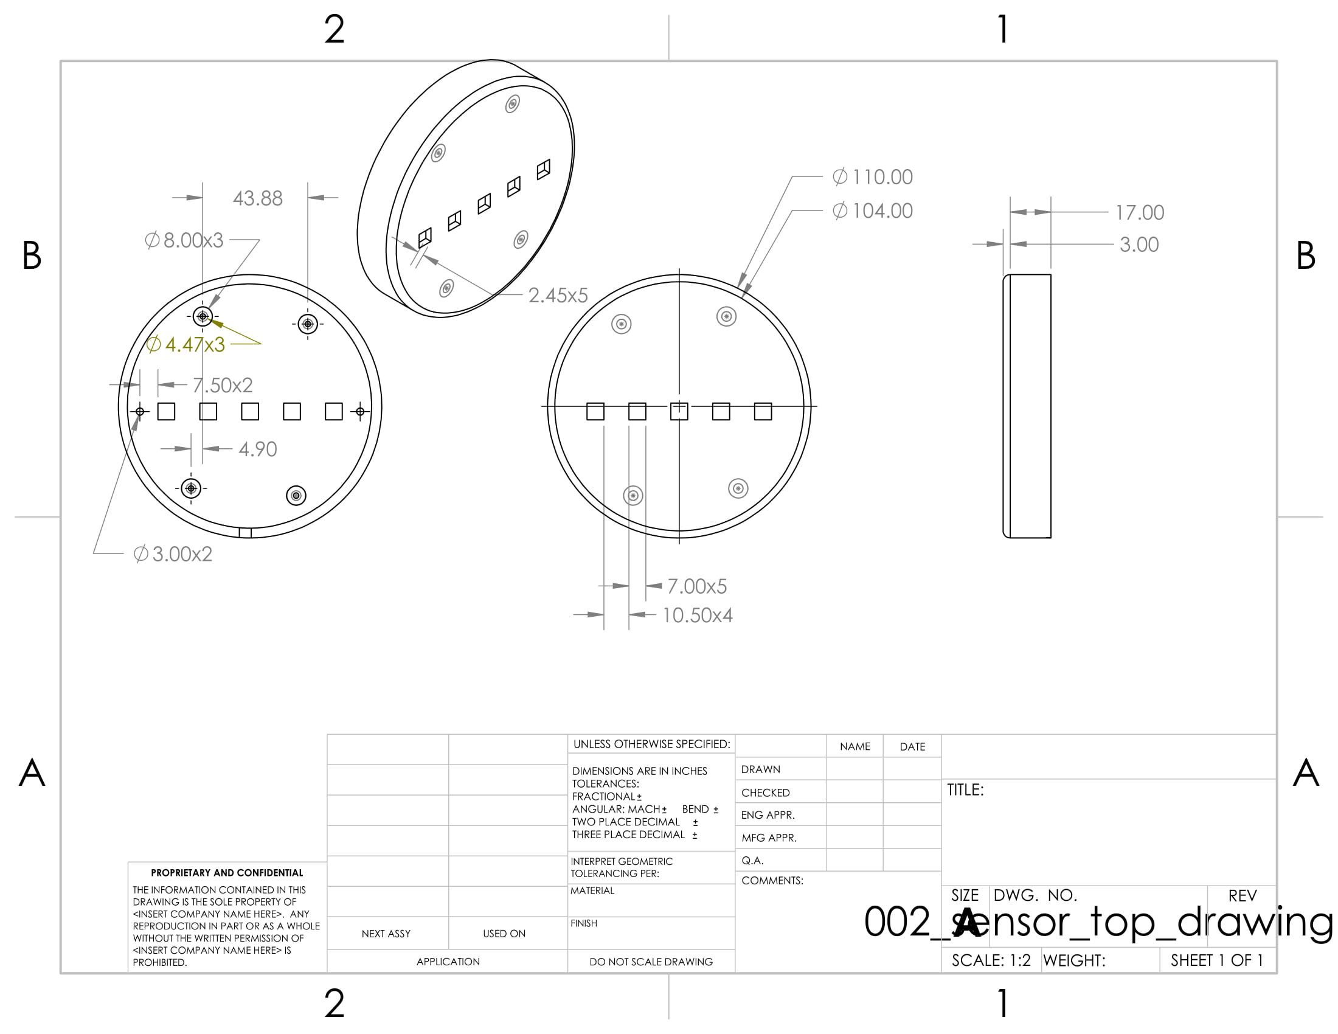
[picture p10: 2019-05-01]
Spring19/Mechanical/Drawings/002_sensor_top.jpg

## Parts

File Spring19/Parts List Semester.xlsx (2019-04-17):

Part | Part Number | Total Cost | Unit Cost | Amount | Project Cost | Website
Capacitive Touch Sensor | 1602 | $7.95 | $7.95 | 7 | $55.65 | Cap Touch Sensor on Adafruit (https://www.adafruit.com/product/1602)
NeoPixel Lights | WS2812B | $20.00 | $0.13 | 5 | $0.67 | NeoPixel on Amazon (https://www.amazon.com/Programmable-Aclorol-Individually-Addressable-Raspberry/dp/B07BKNS7DJ?s=gateway)
Vibrating Mini Motor Disk | 1201 | $1.95 | $1.95 | 3 | $5.85 | Haptic on Adafruit (https://www.adafruit.com/product/1201)
Arduino Nano |  | $12.35 | $4.12 | 1 | $4.12 | Arduino Nano on Amazon (https://www.amazon.com/WYPH-ATmega328P-Microcontroller-Development-Pre-soldered/dp/B07KC9C6H5?s=gateway)
Arduino Uno | A000066 | $20.69 | $20.69 | 1 | $20.69 | Arduino Uno on Amazon (https://www.amazon.com/Arduino-A000066-ARDUINO-UNO-R3/dp/B008GRTSV6?s=gateway)
1k 0603 Surface Mount Resistor | ESR03EZPJ102 | $0.10 | $0.10 | 10 | $1.00 | 1k 0603 Resistor on Digikey (https://www.digikey.com/product-detail/en/rohm-semiconductor/ESR03EZPJ102/RHM1.0KDCT-ND/1762924)
Green Surface Mount LED 1206 | LTST-C230KGKT | $0.34 | $0.34 | 2 | $0.68 | Green LED on Digikey (https://www.digikey.com/product-detail/en/lite-on-inc/LTST-C230KGKT/160-1456-1-ND/386854)
10k Potentiometer |  | $8.99 | $0.90 | 3 | $2.70 | Potentiometer Assortment on Amazon (https://www.amazon.com/MCIGICM-potentiometer-assortment-Breadboard-Potentiometer/dp/B07C3XHVXV?s=gateway)
Through Hole Green LED | 151031VS06000 | $0.16 | $0.16 | 7 | $1.12 | Green LED on Digikey (https://www.digikey.com/product-detail/en/wurth-electronics-inc/151031VS06000/732-5008-ND/4489988)
Relay | EDR201A0500 | $20.88 | $20.88 | 1 | $20.88 | Relay on Mantech (http://www.mantech.co.za/ProductInfo.aspx?Item=35M1803)
 |  |  |  | Total Cost: | $113.35

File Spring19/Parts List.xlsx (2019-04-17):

Part | Part Number | Total Cost | Unit Cost | Amount | Project Cost | Website | Notes
Capacitive Touch Sensor | 1602 | $7.95 | $7.95 | 1 | $7.95 | Cap Touch Sensor on Adafruit (https://www.adafruit.com/product/1602)
NeoPixel Lights | WS2812B | $20.00 | $0.13 | 5 | $0.67 | NeoPixel on Amazon (https://www.amazon.com/Programmable-Aclorol-Individually-Addressable-Raspberry/dp/B07BKNS7DJ?s=gateway) | This is a long strip, only need 5 segments
Vibrating Mini Motor Disk | 1201 | $1.95 | $1.95 | 1 | $1.95 | Haptic on Adafruit (https://www.adafruit.com/product/1201)
Arduino Nano |  | $12.35 | $4.12 | 1 | $4.12 | Arduino Nano on Amazon (https://www.amazon.com/WYPH-ATmega328P-Microcontroller-Development-Pre-soldered/dp/B07KC9C6H5?s=gateway) | 3 Controllers, only need 1
Arduino Uno | A000066 | $20.69 | $20.69 | 1 | $20.69 | Arduino Uno on Amazon (https://www.amazon.com/Arduino-A000066-ARDUINO-UNO-R3/dp/B008GRTSV6?s=gateway)
1k 0603 Surface Mount Resistor | ESR03EZPJ102 | $0.10 | $0.10 | 6 | $0.60 | 1k 0603 Resistor on Digikey (https://www.digikey.com/product-detail/en/rohm-semiconductor/ESR03EZPJ102/RHM1.0KDCT-ND/1762924) | Can be interchanged with any 0603 1k resistor
Green Surface Mount LED 1206 | LTST-C230KGKT | $0.34 | $0.34 | 2 | $0.68 | Green LED on Digikey (https://www.digikey.com/product-detail/en/lite-on-inc/LTST-C230KGKT/160-1456-1-ND/386854) | Can be interchanged with any 1206 Green LED
10k Potentiometer |  | $8.99 | $0.90 | 1 | $0.90 | Potentiometer Assortment on Amazon (https://www.amazon.com/MCIGICM-potentiometer-assortment-Breadboard-Potentiometer/dp/B07C3XHVXV?s=gateway) | Only need 1 10k Potentiometer
Relay | EDR201A0500 | $20.88 | $20.88 | 1 | $20.88 | Relay on Mantech (http://www.mantech.co.za/ProductInfo.aspx?Item=35M1803)
 |  |  |  | Total Cost: | $58.43

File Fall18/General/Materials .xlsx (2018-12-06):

Material | Purpose | Cost
Grove IR Reflective sensor | hand sensing mechanism | 4.9
Particle Photon Board | Wireless communication | 19.7
Planned:
Gooseneck clamp | flexible bedside stand | $26.00
LED strip powered by 3.3V | feedback lights | 2018-10-30

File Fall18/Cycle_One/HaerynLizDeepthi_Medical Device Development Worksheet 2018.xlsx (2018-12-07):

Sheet: Design Context Review
Design Context Review (What do I need to know?)
Priority | Disease State Fundamentals (Physiology, Anatomy, Epidemiology) | Who will research? | Included in Design Context Review so far
7 | What percentage of Americans are hospitalized annually? | Deepthi | X
4 | What is the average length of hospital stay? | Deepthi | X
6 | What is the most common ailment that places people in in-patient care? | Deepthi | X
3 | What is the most common reason a patient would need to call a nurse? | Deepthi | X
5 | What percentage of time is a visitor allowed in the hospital room? | Haeryn
1 | What range encompasses the physical capabilities of stroke victims? | Haeryn
2 | How quickly does a nurse need to answer a call before causing harm to the patient? | Haeryn
Priority | Information about customers (users, payers, regulators)
3 | Where are competitive products being sold -- hospitals, pharmacies, clinics, or online? | Haeryn
1 | How frequently would the patient use the product in a given day? | Deepthi | X
4 | Do our customers fall into a particular age-range? | Deepthi | X
2 | How motivated would users or caretakers be in keeping the solution up and running? | Deepthi | X
Priority | Applicable regulations or standards
5 | What safety standards exists for intra-room and inter-room communication? | Liz
2 | How long should the device be able to last before needing new parts or power supplies? | Liz
1 | How much mobility should the patient need to use the device? | Liz
3 | How will the device motivate users to keep it working? | Haeryn
4 | What are other systems that exist that help communication between patients and nurses? | Deepthi | X
Priority | Technologies that might be used in your design
2 | Can we elimate wires in the design? | Liz
3 | What is the accuracy rate that we are aiming for? | Haeryn
4 | What components can we use to send a communication signal? | Liz
5 | What power source is needed to run the device? | Deepthi | X
6 | Will the communication device be able to communicate a specific want or need? | Deepthi | X
1 | What will compose the user interface or series of interactions/input signals? | Liz
Priority | Competetive products or patents
1 | Is there a more reliable visual system for patients to be monitored? | Liz
3 | Are there competitive devices for people who are unable to speak? | Liz
2 | Who do we need to consult for information about competitive products? | Liz

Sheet: Objectives
 |  | Objectives for Cycle 2
 | Related Specifications |  | (< 300) | Graded Points
 | Brainstorming Objectives
1 | Number of different settings/ modes to adapt to varying hand dexterities; Number of connections from device to power, Time it takes to find and use | Outline a functional decomposition of device | 150
2 | Time it takes to find and use | Pugh Matrix to isolate 2 ways device could potentially alert the user that the call-bell was activated | 150
3 | Time it takes to find and use | Pugh Matrix to isolate 2 ways device could alert the nurse that the call-bell was activated | 150
4 | Time it takes to find and use, Number of different settings/ modes to adapt to varying hand dexterities | Pugh matrix to decide between voice activation, foot pedal, IR sensor, or button. | 200
5 | Battery life | Create list of pros and cons for both a battery supply and a main voltage supply and decide on suitable option | 150
6 | Transmission Range | Research Duke Hospital policy on Bluetooth/WiFi in patient rooms | 100
 | Prototyping Objectives
7 | Number of different settings/ modes to adapt to varying hand dexterities, Weight of device | Detailed sketch of all components of sensor and bedside stand/attachment | 200
8 | Signal transmission | Draw a code block diagram | 200
9 | Number of different settings/ modes to adapt to varying hand dexterities | After choosing mechanism in Objective 5, low fidelity prototype mechanism for voice activation, button, or IR sensor. | 350
10 | Signal transmission | Configure wireless connection (e.g. Particle board or Bluetooth serial module) with at least one remote signal receiver | 350
 |  | TOTALS (= 2000) | 2000

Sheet: Market Analysis
Market Analysis (Who is my customer?)
 | Potential Market Segments | Estimated Market Size (number of beds) | Reference/Reasoning/assumptions | Competitive Products/Solutions | Willingness to pay | Reference/Reasoning/assumptions | Predicted Total Addressable Market
1 | Ambulatory Surgery Centers | 89420 | There are 5,260 ambulatory surgery centers with a mean number of 17 beds per center [6] and [7] | Nurses circulating at regular intervals and call systems with buttons | $150/bed | These centers are usually already using a competitive system which on average costs $150/bed (calculated by comparing call systems at the bottom of chart) | $13413000
2 | Nursing/Retirements Homes | 1689120 | There are 15,640 homes in the United States, most of which are for profit, that house the elderly with a mean of 108 beds per center [11] | Very basic Call systems with single buttons | $25/bell [9] | Using simple call systems to combat deterioration in cognition. [9] | $42228000
3 | Neurocritical Care Units (NCUs) | 1752 | There are 73 NCU in the US [1] with an estimated number of 24 beds per unit [8] | Constant monitoring because of high risk and possible lack of consciousness; call systems with hard buttons | $150/bed | These centers are usually already using a competitive system which on average costs $150/bed | $262800
4 | At home care for patients | 4900000 | About 4.9 million patients that recieved care at some point in a given year from 12,400 agencies [2]. | Manual Bells | $7/bell [10] | Assuming one standard bell ($7) per patient receiving care [10] | $34300000
5 | Palliative Care Units | 36890 | Approximately 2/3 of all hospitals report having a palliative care unit; 5,534 Hospitals in America and that there are 10 beds per unit [3][4] | Call systems with hard buttons | $150/bed | These centers are usually already using a competitive system which on average costs $150/bed | $5533500
 | Sources:
 | 1. https://www.ncbi.nlm.nih.gov/pubmed/22045246
 | 2. https://www.cdc.gov/nchs/fastats/home-health-care.htm
 | 3. https://www.ncbi.nlm.nih.gov/pmc/articles/PMC4651439/
 | 4. https://www.aha.org/statistics/fast-facts-us-hospitals
 | 5. https://health.usnews.com/wellness/articles/2016-11-16/how-to-pay-for-nursing-home-costs
 | 6. https://www.beckersasc.com/asc-transactions-and-valuation-issues/number-of-ambulatory-surgery-centers-approaches-number-of-hospitals-nationwide.html
 | 7. https://www.ncbi.nlm.nih.gov/pmc/articles/PMC2980831/
 | 8. https://neurology.duke.edu/divisions/critical-care-and-vascular-neurology/neurocritical-care-unit-duke-medical-pavilion-8e
 | 9. https://www.amazon.com/Smart-Caregiver-Buttons-Wireless-Pager/dp/B0032FMSWS
 | 10. https://www.amazon.com/gp/product/B0769WH8F2
 | 11. https://www.cdc.gov/nchs/fastats/nursing-home-care.htm
 | HOSPITAL CALL SYSTEMS:
 | Company | Price for system | Number of Units | Price/per unit | Type of system | Link
 | BEC Integrated | $3128.00 | 24 | $130.33 | Wireless call bell system | https://becintegrated.com/wireless-nursecall-for-hospitals-with-24-pendants-and-call-bell-system?site=google_base
 | BEC Integrated | $2048.00 | 12 | $170.67 | Visual alert system, connected to wall power | https://becintegrated.com/tektone-ttnc110-24-1?site=google_base
 | Patterson Medical |  | 1 | $124.21 | Quadraplegic Nurse Call system | https://www.devinemedical.com/4130-Quadriplegic-Nurse-Call-Switch-with-Cord-p/4130.htm
 | Economat Nurse Call Monitor |  | 1 | $166.99 | Notifies nurse when patient exits bed/chair | https://www.medexsupply.com/patient-care-patient-monitors-and-alarms-economat-nurse-call-monitor-x_pid-10591.html?pid=10591
 | Average |  |  | $148.05

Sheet: Cust. Needs and Prob St.
Customer Needs (What does my customer need?)
Number | Need | Priority
User Needs
 | The patient can conveniently find the device but not have it be in the way when not needed | 1
 | The device needs to be easily accessible without needing to walk to it | 3
 | The device needs to reliably contact the nurse | 4
 | The device needs to require few battery changes or cords connected to the wall | 5
 | The device needs to be understood by patients with limited cognitive ability. | 2
Payer Needs
 | The device has a similar cost to competitive call systems | 1
 | Should be able to be produced/purchased in bulk so hospitals can provide device for each patient room | 2
 | The alert mechanism should be clear, consistent, reliable | 3
 | The alert mechanism should not be unreasonable or irritating | 4
Regulatory/Standards Needs
 | The call system complies with regulations already met by the DMP | 2
 | The device does not cause any adverse health effects, or pose a trip or fall hazard to the patients | 1
 | Software on the device should meet IEC Medical Device Software Standards | 3
Problem/Need Statement:
We will design a way to: | improve patient-nurse communication
in: | patients with limited mobility
that: | increases accessibility to assitance while reducing the number of false alerts
No. | Type of need | Need
1 | patient | easily accesible for patient with limited mobility
2 | patient | can be understood by patients with limited cognitive ability
3 | patient | will not be in the way when not in use
4 | patient | is lightweight
5 | nurse | transmits the signal to multiple receivers
6 | nurse | quickly transmits the signal to nurses
7 | nurse | reduces the amount of false-positives going to the nurses's station
8 | nurse | durable and can withstand accidents
9 | nurse | reduces excessive wiring
10 | payer | has similar cost to other competitive nurse call systems
11 | payer | can be produced and purchased in bulk so hospitals can use in each patient room
12 | regulatory | complies with regulations met by the DMP
13 | regulatory | The device does not cause any adverse health effects, or pose a trip or fall hazard to the patients
14 | regulatory | software meets IEC Medical Device Software Standards

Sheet: Pugh Matrices
Pugh Matrix
 | Concept Name: | Wireless Device | Sensor Based call bell- no button press | Various buttons/functions on one bell | Battery powered-device | Eye-tracking based call-bell | Call-bell on attachable bedside stand | Wall-connected Rechargeable device | Voice-activated call bell | Foot-pedal call-bell | Current Inpatient Call-bell (remote with call-bell on TV remote)
 | Less wires | 1 | 0 | 0 | 1 | 0 | 0 | -1 | 1 | -1 | 0
 | cheap | -1 | -1 | 1 | -1 | -1 | 1 | 1 | -1 | 0 | 0
 | Reduce false alerts to nurses | 0 | -1 | 1 | 0 | -1 | 1 | 0 | 1 | 0 | 0
 | Power the device consistently | 0 | 0 | 0 | -1 | 0 | 0 | 1 | 0 | 0 | 0
 | Increased accessibility to patients with limited finger-dexterity | 0 | 1 | -1 | 0 | 1 | 0 | 0 | 1 | 1 | 0
 | Ability to communicate various things to nurse | 0 | 0 | 1 | 0 | 0 | 0 | 0 | 1 | 0 | 0
 | Totals | 0 | -1 | 1 | -1 | -1 | 2 | 1 | 2 | 0 | 0

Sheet: LBM
Labor, Burden and Materials (LBM) Cost Analysis
 | Burdened Labor Rate: | $33.00 | per hour
 | Process Step | Material | Quantity | Cost at Full Scale | # of people | Duration of Task (hrs) | Cost | Notes
 | e.g. Mounting front bars to base | Front bars | 2 | $75.00 | 2 | 0.5 | $183.00
 |  | Base | 1 | $100.00 |  |  | $100.00
 |  | Adhesive | 1 | $5.00 |  |  | $5.00
 | e.g. Task #2 |  |  |  |  |  | $0.00
 | 3D printing casing | Plastic | 1 | $5.00 | 1 | 5 | $170.00
 |  |  |  |  |  |  | $0.00
 |  |  |  |  |  |  | $0.00
 |  |  |  |  |  |  | $0.00
 |  |  |  |  |  |  | $0.00
 |  |  |  |  |  |  | $0.00
 | TOTAL |  |  |  |  |  | $458.00

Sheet: IP
IP Strategy
 | Relevant Patents:
 | Patent Number | Title | Inventors/Assignees | Notes
 | US3848249A | Apparatus actuating and nurse call system | S Meiri/ Northwestern University | Uses breath-operated switch for patients with limited mobility in the hospital
 | US5561412A | Patient/Nurse Call system | Joseph H. Novak/ Hill-Rom, Inc. | A patient/nurse call system for a hospital includes patient stations capable of generating hospital calls and a remote master station which prioritizes and stores the calls.
 | US8296383B2 | Voice Activated "Nurse" Call Bell | George Dib & Rachel Starr/ University of Rhode Island | Voice activated call-bell helping patients with limited mobility
 | US4484367A | Nurse call apparatus | Betty Jenkins/ Jenkins Betty | Nurse call bell holder
 | US5838223A | Patient/nurse call system | Ulrich/ Hill-Rom, Inc. | Wireless call bell system
 | IP Risk: | Medium

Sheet: FMEA
FMEA
 | Potential Failure Mode | Cause(s) | Effect(s) | Probability of Occurance (Frequent-Improbable) | Severity (Catastrophic-Negligible) | Risk Index | Acceptable? | Mitigation Plan
1 | e.g. Dislodgement of electrode from chest | Poor surface preparation, excessive sweat, hair, cord pulled, patient movement | Poor to no electrical signal, patient no longer monitored | Frequent | Significant | 3 | No | Select stronger, water-resistant adhesive for electrode design
2 | Call-bell does not alert nurse's station | Inneffective wireless or hardwire communication | Nurse is not notified when patient is in need | Occasional | Significant | 6 | No | Ensure that call-bell has few connections to plug in/is always charged
3 | Call-bell sends false alert to nurse's station | Sensor/voice-activation/button is too sensitive | Nurse gets notified too frequently, potential boy cried wolf situation | Probable | Marginal | 9 | No | Develop check system within call bell (patient has to hover hand over sensor/ tap button twice, voice activation can ask "do you want to call ________?")
4 | Call-bell cannot be reached/used by patient | Out of reach, requires high degree of finger-dexterity or cognitive ability | patient cannot communicate need to nurse | Probable | Significant | 5 | No | Voice activation/sensor based call bell- attached to bed side so it is easily accessible
5
6
7
8
9
10
11

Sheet: Risk Register
Risk Register
 | Project Risk Title | Resource/Time Risk if Triggered (1-5) | Technical Challenge (1-5) | Composite Risk Index
 | Button does not activate/page nurse | 4 | 5 | 20
 | Bell is not plugged in | 5 | 1 | 5
 | Bell is too sensitive | 3 | 5 | 15
 | Patient cannot push button | 4 | 4 | 16
 |  |  |  | 0
 |  |  |  | 0
 |  |  |  | 0
 |  |  |  | 0

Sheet: Clin Reg Strategy
Regulatory and Clinical Strategy
 | 6 Key Questions: | Answers:
 | Is this a medical device? If so, what class? | Yes, a class I medical device (not sure about this)
 | What devices could be considered similar or “predicate devices”? | Pancake call-bell, Call-bell attached to TV remote, single-button call bell.
 | What would be the most appropriate regulatory pathway for this device?
 | What clinical trial might be needed for your product and what would it’s purpose be? (Regulatory approval, Reimbursement, Marketing, etc.) Choose one. | Regulatory approval?
 | What design/model should each study be? (pilot, registry, randomized, controlled, etc.) | Pilot
 | Determine one primary and one secondary endpoints for the trial you are considering.

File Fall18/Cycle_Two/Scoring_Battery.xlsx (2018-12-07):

MediCall | Pugh matrix for determinig device power mechanism
Deepthi Nacharaju
Haeryn Kim
Lizbeth Leapo
Category | Weighted score (1-5) | AA battery | Rechargeable AA battery | Wall power
Size | 1 | 1 | 1 | -1
Rechargeability | 2 | -1 | 1 | 1
Wireless | 5 | 1 | 1 | -1
Safety (Decreased performance on low power) | 4 | 1 | 1 | -1
Cost | 3 | -1 | -1 | 1
Install Unnecessary | 1 | 1 | 1 | -1
Sum of Positives |  | 4 | 5 | 2
Sum of Negatives |  | -2 | -1 | -4
Overall Total |  | 2 | 4 | -2
Weighted Total |  | 6 | 10 | -6
Among options of AA rechargeable batteries: |  |  |  |  | Rank
Battery | Cheapest market price/unit ($) | Capacity (mAh) | Charging limit (times) | Runtime on one charge | Price | Capacity | Charging cycle limit | Runtime | Total
Panasonic Eneloop Pro | $6.58 | 2550 | 500 | 10 hr 45 min | 1 | 5 | 4 | 5 | 15
AmazonBasics High Capacity | $1.87 | 2400 | 500 | 9 hr 45 min | 5 | 3 | 4 | 4 | 16
Duracell Rechargeable | $3.62 | 2450 | 400 | 9 hr 33 min | 2 | 4 | 3 | 3 | 12
AmazonBasics Rechargeable Batteries | $2.32 | 2000 | 1000 | 8 hr 20 min | 3 | 2 | 5 | 2 | 12
Energizer Recharge Universal | $2.00 | 2000 | 1000 | 8 hr 17 min | 4 | 2 | 5 | 1 | 12

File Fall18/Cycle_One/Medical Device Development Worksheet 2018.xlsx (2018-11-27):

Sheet: Design Context Review
Design Context Review (What do I need to know?)
Priority | Disease State Fundamentals (Physiology, Anatomy, Epidemiology) | Who will research?
1 | e.g. How many people in the US have this disease? | Eric
2
3
Priority | Information about customers (users, payers, regulators)
1 | e.g. How are the cost of medical devices reimbursed in a hospital? | Mark
2
3
Priority | Applicable regulations or standards
1 | e.g. What safety standards exists for the electronics that might be used in our product? | Eric
2
3
Priority | Technologies that might be used in your design
1 | e.g. What are the pros/cons of various wireless data transmission protocols? | Mark
2
3
Priority | Competetive products or patents
1 | e.g. What products are considered my primary competitors? | Eric
2
3

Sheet: Market Analysis
Market Analysis (Who is my customer?)
 | Potential Market Segments | Estimated Market Size | Reference/Reasoning/assumptions | Competitive Products/Solutions | Willingness to pay | Reference/Reasoning/assumptions | Predicted Total Addressable Market
1 | e.g. College students within the US who suffer sleep deprivation | e.g.1.25M students/year | e.g. There are 20 million college students in the US (DOE Statistics) and we assume that during 1/8 of the academic year (in weeks during midterms and finals) atlease half of students are sleep-deprived. | e.g. Time management strategies, coffee, naps, etc. | Students would be willing to pay 4$ for 2 hours of relief from sleep deprivation. They would use this ~20 times/year | Based on the average price of coffee, which students currently pay | 10%
2
3
4
5

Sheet: Cust. Needs and Prob St.
Customer Needs (What does my customer need?)
Number | Need | Priority
User Needs
 | e.g. The phone application reduces patient waiting time in the hospital | 1
Payer Needs
 | e.g. The phone app has a similar cost to competitive apps | 3
Regulatory/Standards Needs
 | e.g. The phone app complies with HIPAA regulations | 2
Problem/Need Statement:
We will design a way to: | (Problem)
in: | (Population)
that: | (Desired, measurable outcome)

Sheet: HOQ, Specs
House of Quality, Functional Specs
 |  | Spec #1 | Spec #2 | Spec #3 | Spec #4 | Spec #5 | Spec #6
Priority | CUSTOMER REQUIREMENTS/NEEDS | Duration of a 0-60mph acceleration
1 | The vehicle must accelerate quickly. | X
2
3
4
5
6
7
8
 | Competive Values | 4.5 sec
 | Marginal Value | 4.5 sec
 | Ideal Value | 4.0 sec

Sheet: Pugh Matrices
Pugh Matrix
 | Concept Name: | Concept 1 | Concept 2 | Concept 3 | Concept 4 (Standard)
 | Spec 1 | 0 |  |  | 0
 | Spec 2 | 1 |  |  | 0
 | Spec 3 | -1 |  |  | 0
 | Spec 4 | -1 |  |  | 0
 | Totals | -1 | 0 | 0 | 0

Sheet: LBM
Labor, Burden and Materials (LBM) Cost Analysis
 | Burdened Labor Rate: | $33.00 | per hour
 | Process Step | Material | Quantity | Cost at Full Scale | # of people | Duration of Task (hrs) | Cost | Notes
 | e.g. Mounting front bars to base | Front bars | 2 | $75.00 | 2 | 0.5 | $183.00
 |  | Base | 1 | $100.00 |  |  | $100.00
 |  | Adhesive | 1 | $5.00 |  |  | $5.00
 | e.g. Task #2 |  |  |  |  |  | $0.00
 |  |  |  |  |  |  | $0.00
 |  |  |  |  |  |  | $0.00
 |  |  |  |  |  |  | $0.00
 |  |  |  |  |  |  | $0.00
 |  |  |  |  |  |  | $0.00
 |  |  |  |  |  |  | $0.00
 | TOTAL |  |  |  |  |  | $288.00

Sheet: IP
IP Strategy
 | Relevant Patents:
 | Patent Number | Title | Inventors/Assignees | Notes
 | US 600,0000 | A method for sealing paravalvular leaks | Palmeri, Richardson/Duke | Very similar - these guys are smart.
 | IP Risk: | (High, Medium, Low)

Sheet: FMEA
FMEA
 | Potential Failure Mode | Cause(s) | Effect(s) | Probability of Occurance (Frequent-Improbable) | Severity (Catastrophic-Negligible) | Risk Index | Acceptable? | Mitigation Plan
1 | e.g. Dislodgement of electrode from chest | Poor surface preparation, excessive sweat, hair, cord pulled, patient movement | Poor to no electrical signal, patient no longer monitored | Frequent | Significant | 3 | No | Select stronger, water-resistant adhesive for electrode design
2
3
4
5
6
7
8
9
10
11

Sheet: Risk Register
Risk Register
 | Project Risk Title | Resource/Time Risk if Triggered (1-5) | Technical Challenge (1-5) | Composite Risk Index
 | Adhesive won't hold | 3 | 5 | 15
 |  |  |  | 0
 |  |  |  | 0
 |  |  |  | 0
 |  |  |  | 0
 |  |  |  | 0
 |  |  |  | 0
 |  |  |  | 0

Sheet: Clin Reg Strategy
Regulatory and Clinical Strategy
 | 6 Key Questions: | Answers:
 | Is this a medical device? If so, what class?
 | What devices could be considered similar or “predicate devices”?
 | What would be the most appropriate regulatory pathway for this device?
 | What clinical trial might be needed for your product and what would it’s purpose be? (Regulatory approval, Reimbursement, Marketing, etc.) Choose one.
 | What design/model should each study be? (pilot, registry, randomized, controlled, etc.)
 | Determine one primary and one secondary endpoints for the trial you are considering.

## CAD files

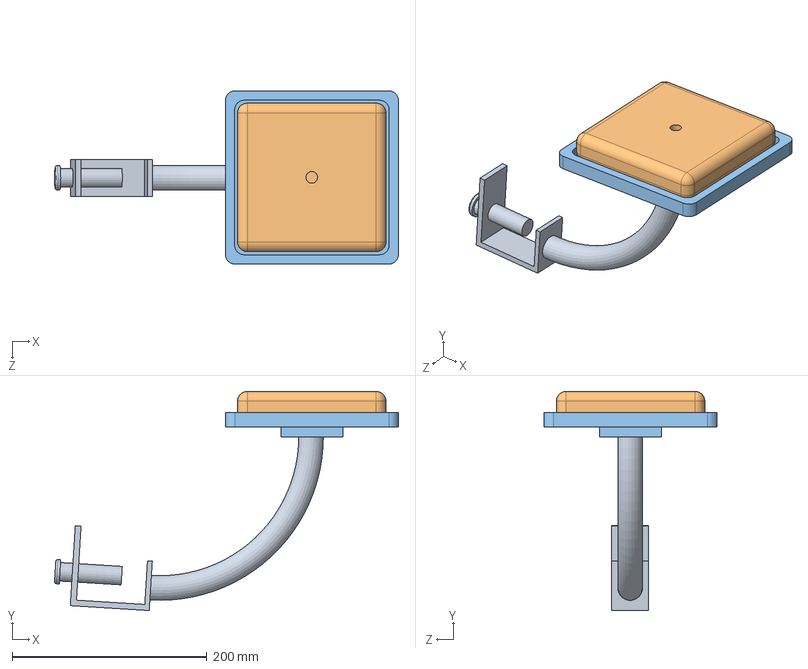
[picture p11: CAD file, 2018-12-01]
Fall18/Mechanical/strokesensorassembly.SLDASM
353.1 x 224.9 x 177.8 mm
clamp
sensor
sensor holder

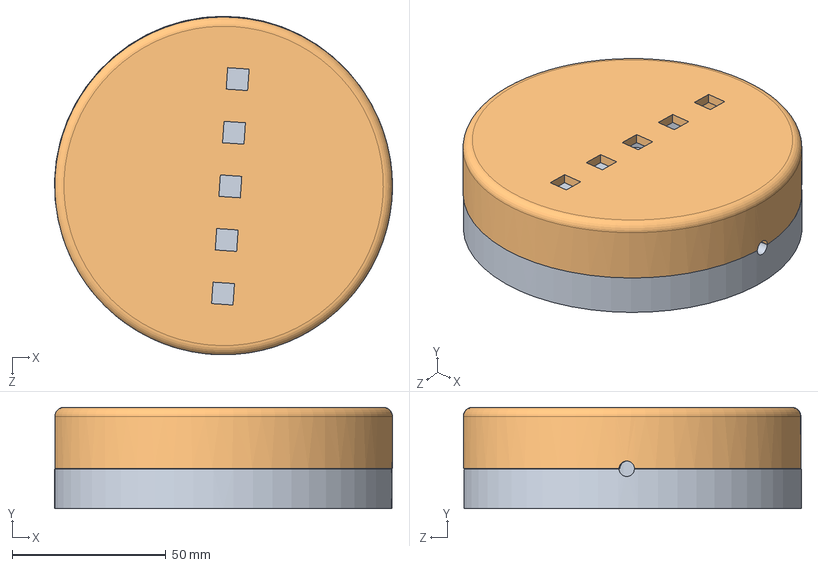
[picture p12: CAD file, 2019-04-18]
Spring19/Appendices/Appendix E/MEDICALL CAD/sensor_assembly.SLDASM
110.1 x 33.0 x 110.2 mm
001_sensor_bottom
002_sensor_top

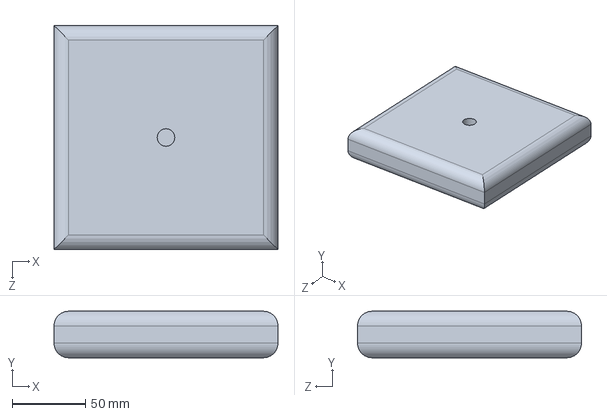
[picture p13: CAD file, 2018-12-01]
Fall18/Mechanical/sensor.SLDPRT
152.4 x 31.8 x 152.4 mm

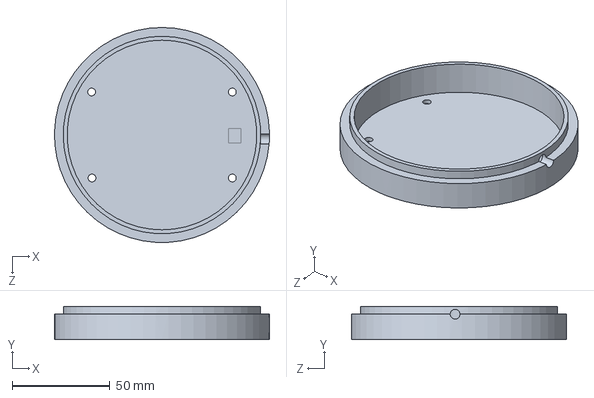
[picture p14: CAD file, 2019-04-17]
Mechanical/medicallbottom2.SLDPRT
110.0 x 17.0 x 110.0 mm

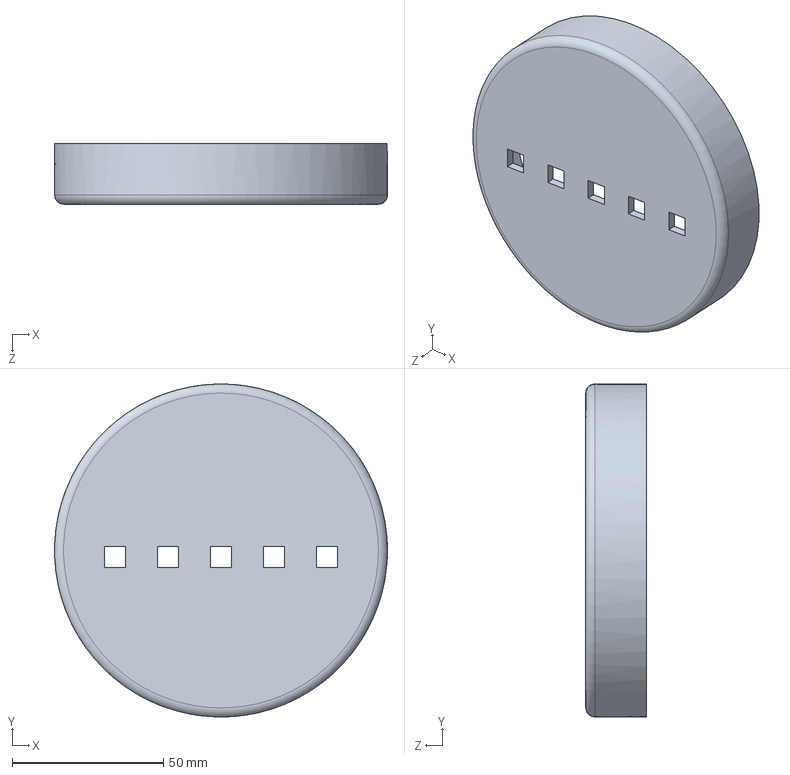
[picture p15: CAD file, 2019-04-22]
Spring19/Appendices/Appendix E/MEDICALL CAD/002_sensor_top.SLDPRT
110.0 x 110.0 x 20.0 mm

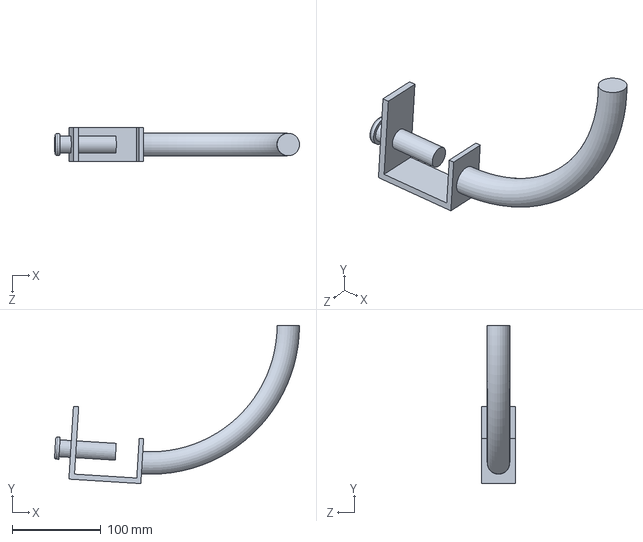
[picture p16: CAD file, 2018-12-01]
Fall18/Mechanical/clamp.SLDPRT
276.0 x 178.2 x 38.1 mm

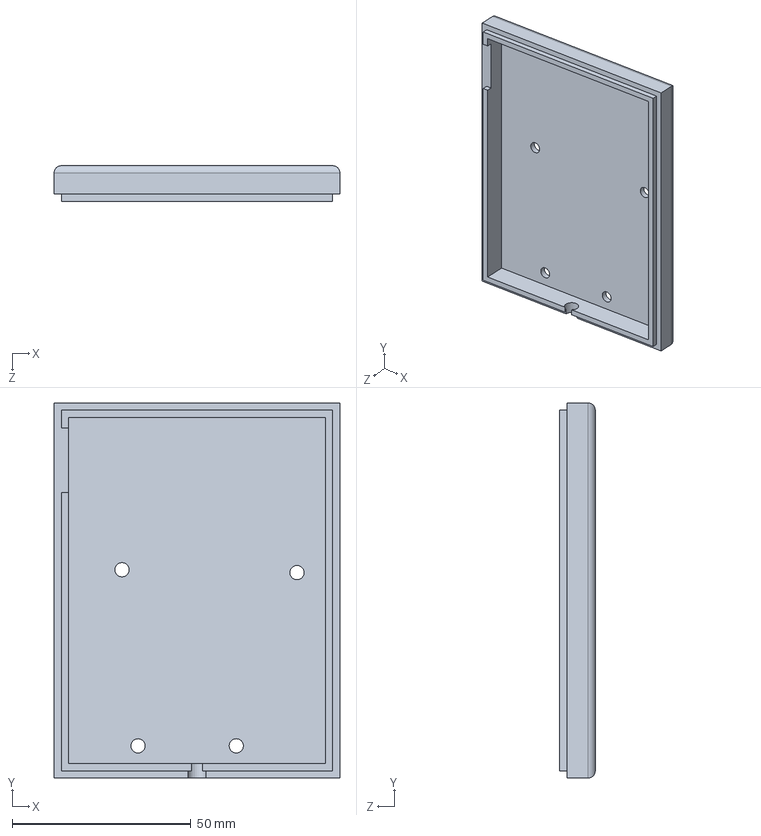
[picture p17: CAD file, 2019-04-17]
Mechanical/newboxbottom.SLDPRT
80.0 x 105.0 x 10.0 mm

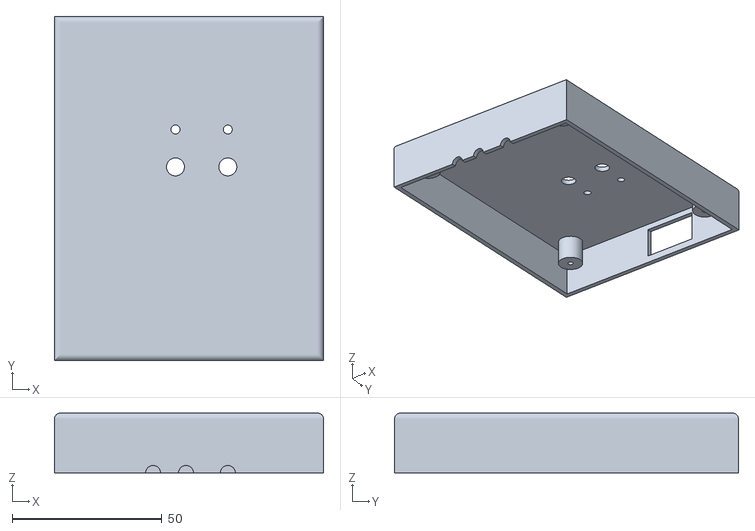
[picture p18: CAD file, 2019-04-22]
Spring19/Appendices/Appendix E/MEDICALL CAD/004_box_top.STL
90.0 x 115.0 x 20.0

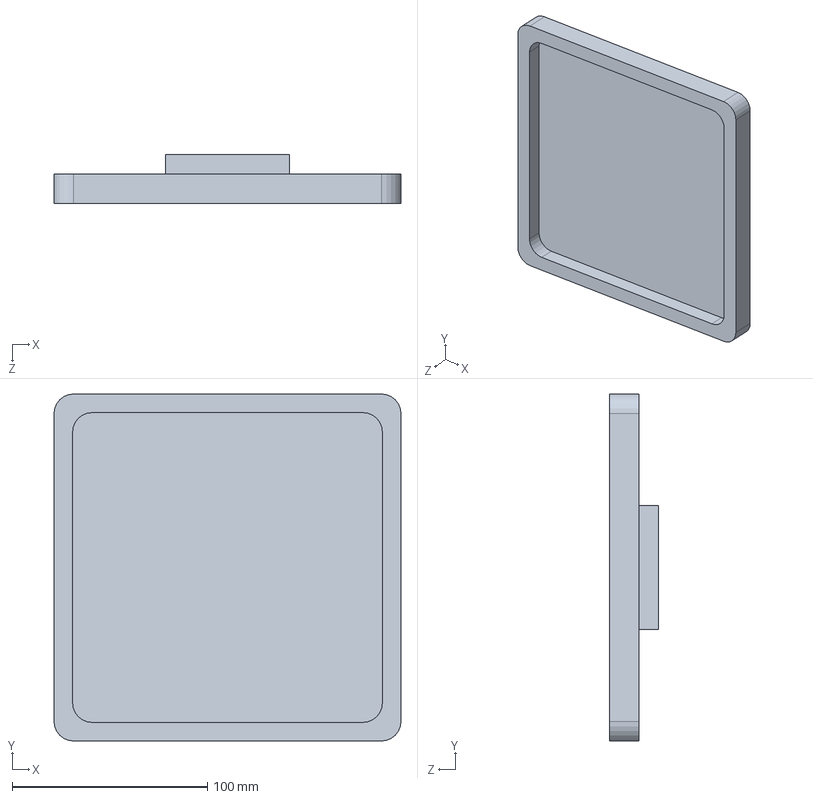
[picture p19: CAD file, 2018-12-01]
Fall18/Mechanical/sensor holder.SLDPRT
177.8 x 177.8 x 25.0 mm

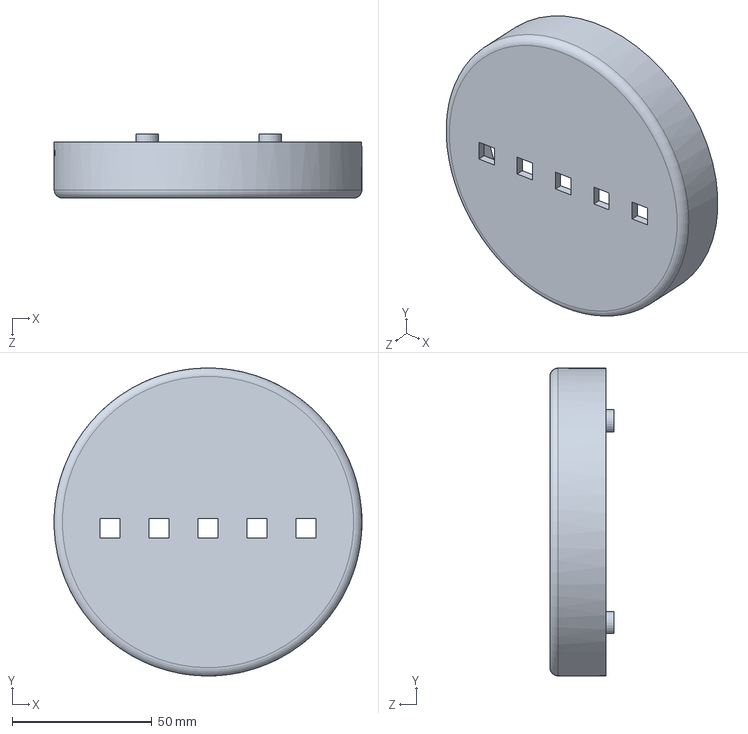
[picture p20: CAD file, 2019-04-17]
Mechanical/medicalltop2.SLDPRT
110.0 x 110.0 x 23.0 mm

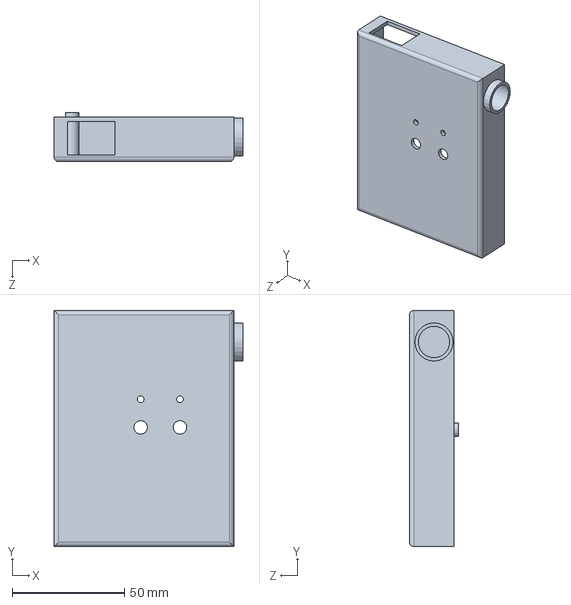
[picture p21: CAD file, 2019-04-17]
Mechanical/newboxtop.SLDPRT
84.0 x 105.0 x 22.0 mm

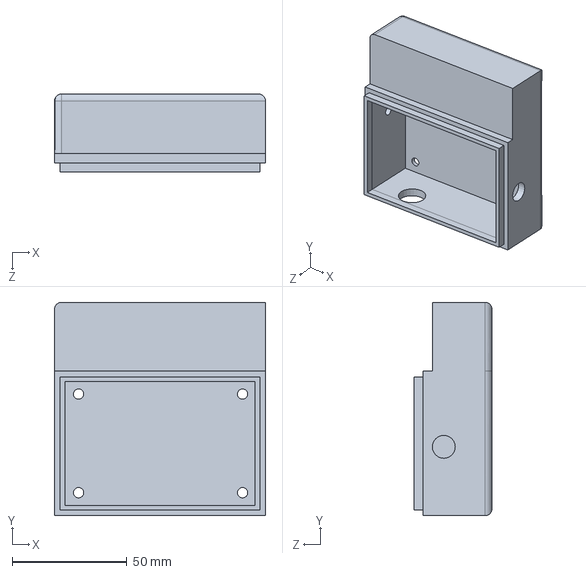
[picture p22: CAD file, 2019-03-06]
Mechanical/medcallboxbottom2.SLDPRT
92.0 x 93.0 x 34.0 mm

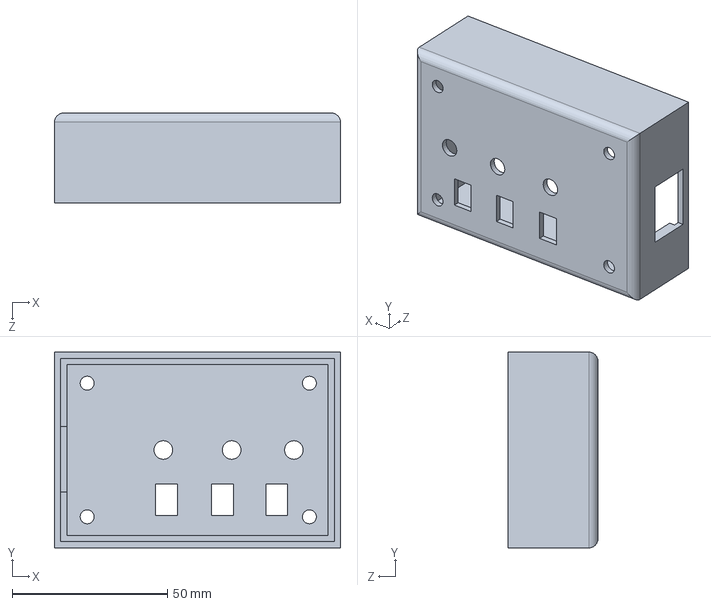
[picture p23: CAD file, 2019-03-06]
Mechanical/medcallboxtop3.SLDPRT
92.0 x 63.0 x 29.0 mm

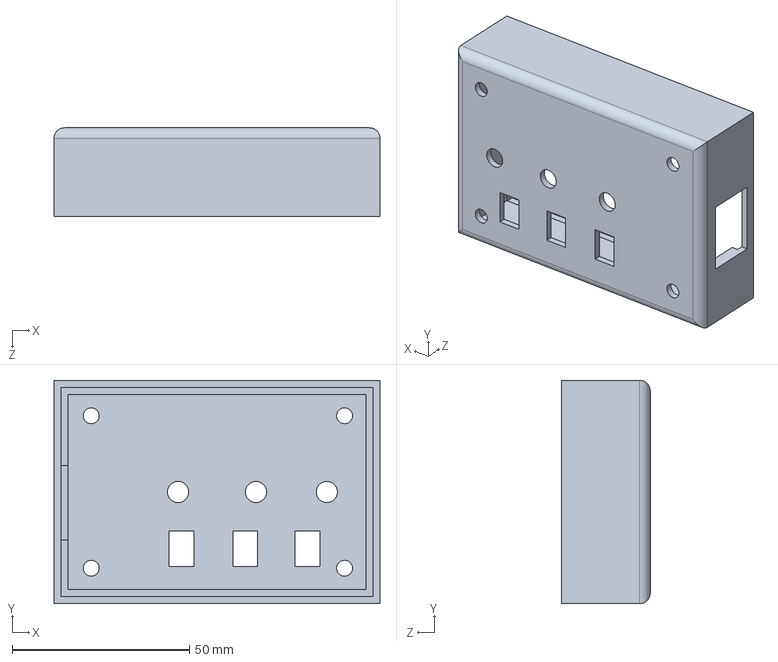
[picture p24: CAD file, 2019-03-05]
Mechanical/medcallboxtop2.SLDPRT
92.0 x 63.0 x 25.0 mm

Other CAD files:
Spring19/Appendices/Appendix E/MEDICALL CAD/Cut-Extrude10.sldprt
Spring19/Appendices/Appendix E/MEDICALL CAD/001_sensor_bottom.SLDPRT
Mechanical/medcallboxbottom.SLDPRT
Mechanical/medicallbottom.SLDPRT
Mechanical/CADsensor part.SLDPRT
Mechanical/CADsensortop.SLDPRT
Mechanical/lightholder.SLDPRT
Mechanical/medcallboxtop.SLDPRT
Mechanical/medicallbottom2.STL
Mechanical/medicalltop.SLDPRT
Mechanical/medicalltop.STL
Mechanical/medicalltop2.STL
Mechanical/newboxbottom.STL
Mechanical/newboxtop.STL
Mechanical/sensorbottom.SLDPRT
Spring19/Appendices/Appendix E/Drawings/001_sensor_bottom_drawing.SLDDRW
Spring19/Appendices/Appendix E/Drawings/002_sensor_top_drawing.SLDDRW
Spring19/Appendices/Appendix E/Drawings/003_box_bottom_drawing.SLDDRW
Spring19/Appendices/Appendix E/Drawings/004_box_top_drawing.SLDDRW
Spring19/Appendices/Appendix E/MEDICALL CAD/002_sensor_top.STL

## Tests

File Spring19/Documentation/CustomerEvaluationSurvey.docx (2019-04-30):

Device Evaluation Form

Medicall Nurse Call Bell

Date: ______________________

Number of times used: ________________________

Your occupation or specialty: _______________________

1. Did you receive training in how to use this product?

☐ Yes [Go to next question] | | | | ☐ No [Go to question 4]

2. Who provided this instruction? (Check all that apply.)

☐ Product representative | | ☐ Hospital staff | | | ☐ Other

3. Was the training you received adequate?

☐ Yes | | | | ☐ No

4. Describe the range of mobility of the patient.

Mobile | Partial paralysis (10cm) | | Partial paralysis (1m) | | | Full paralysis

Please answer all questions that apply to your duties and responsibilities. If a question does not apply to your duties and responsibilities, please leave it blank.

| During the Pilot Test of this Device . . . | Strongly Disagree | Disagree | Neutral | Agree | Strongly Agree
5. | The time it took to initiate a call was faster than that of a conventional call button. | 1 | 2 | 3 | 4 | 5
6. | The device was easy to find. | 1 | 2 | 3 | 4 | 5
7. | The device placed less false calls than conventional call buttons. | 1 | 2 | 3 | 4 | 5
8. | The device had similar number of wires as conventional call buttons. | 1 | 2 | 3 | 4 | 5
9. | The device provided multiple modes of feedback. | 1 | 2 | 3 | 4 | 5
10. | The device performed reliably. | 1 | 2 | 3 | 4 | 5
| During the Pilot Test of this Device . . . | Strongly Disagree | Disagree | Neutral | Agree | Strongly Agree
11. | The device not self-activate without my intention. | 1 | 2 | 3 | 4 | 5
12. | I feel safe using this device. | 1 | 2 | 3 | 4 | 5
13. | The device did not increase patient discomfort. | 1 | 2 | 3 | 4 | 5
14. | The device improved my daily load of tasks. | 1 | 2 | 3 | 4 | 5
15. | The device did not cause me to change any way I worked with the patients. | 1 | 2 | 3 | 4 | 5
16. | I could have used this product without special training. | 1 | 2 | 3 | 4 | 5
17. | This device is cost efficient. | 1 | 2 | 3 | 4 | 5
18. | The delay to activation on the device is appropriate. | 1 | 2 | 3 | 4 | 5
19. | The device is easily cleaned. | 1 | 2 | 3 | 4 | 5
20. | The device meets my clinical needs. | 1 | 2 | 3 | 4 | 5
21. | The device is safe for clinical use. | 1 | 2 | 3 | 4 | 5

Additional comments for any responses of “Strongly Disagree” or “Disagree”: _____________

____________________________________________________________________________________________________________________________________________________________

______________________________________________________________________________

______________________________________________________________________________

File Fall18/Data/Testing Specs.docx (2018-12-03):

Testing Specs

Spec #1: User studies with either us or patients in the hospital

Spec #2: Place by our own beds and see the number of times we trigger it during normal movement

Spec #3: This can be counted

Spec #5: This can also be counted; Need to come up with the number of settings we ideally want to have

Spec #6: Move the device from the receiver at different distances and ensure that the signal is still transmitted

Spec #4: Set device off X number of times with a fixture to see when it dies and also leave it running idle and see how long it will run for

Spec #7 add varying levels of water to the sensor and see when it stops working; try cleaning it and make sure it functions

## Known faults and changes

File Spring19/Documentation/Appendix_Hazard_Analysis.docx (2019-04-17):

Notes from Kevin’s presentation:

You will evaluate your projects to identify:

  - Physical Hazards
  - Fault Hazards
  - Operational Hazards
  - Expected Use and Foreseeable Misuse

Quantify Hazards and Assess Risk

Redesign, Guard or Warn

Potential Physical or Fault Hazard?

Physical

- Electricity (Shock)‏
- Sharpness (Cuts)‏
- Pieces (Choking)‏
- Temperature (Hot and Cold)‏
- Stability (Tipping)‏
- Sounds (Intensity)
- Light (Intensity)

Fault

- Buttons, Switches, Connectors
- Bad Solder Joint
- Fastener Failure
- Component Failure
- Fatigue
- Logic Error
- Programming Bug

Operational/User

Expected Use/Forseeable Misuse

- Use in an unintended environment
- Use by children
- People who do not speak the language
- People who are cognitively impaired
- People who display destructive behaviour

IV

IV

IV

IV

Incredible

III

III

IV

IV

Improbable

II

III

III

IV

Remote

I

II

III

III

Occasional

I

I

II

III

Probable

I

I

I

II

Likely

Catastrophic

Critical

Marginal

Negligible

Occurrence

Severity of Consequence

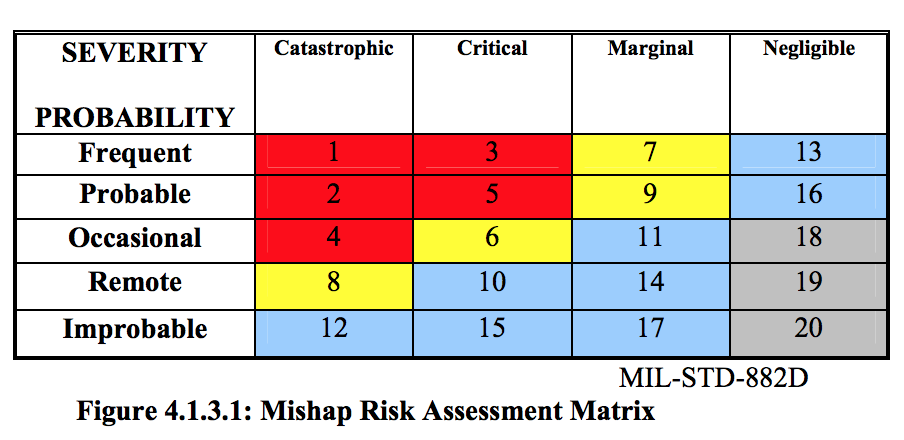
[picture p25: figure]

APPENDIX A – HAZARD IDENTIFICATION & RISK DETERMINATION

Item | Hazard | Cause | Unmitigated Risk Level | Prevention/Mitigation | Potential Impact | Mitigated Risk
1. | Tripping | Extension cord | Level 2 Critical Occasional | Tape/fix to the ground Houskeeping to minimize trip hazards | Fall Sprains | Level 19 Negligible Remote
2. | Choking(Strangulation) – foreseeable misuse | Extension cord | Level 3 Catastrophic Improbable | Tape/fix out of reach of patient Training of personnel in hazard recognition and support | Death of asphyxiation | Level 12 Catastrophic Improbable
3. | Stability(Tipping) | Clamp | Level 3 Negligible Occasional | | Physical impact on device
4. | Hot Device Temperature | Battery | Level 3 Critical Remote | Heatsink CAD or PCB | Mild burn upon elongated touch | Level 19 Negligible Remote
5. | Environmental | Spills | Level 3 Marginal Remote | Airtight enclosure | Burn internal components of device | Level 19 Negligible Remote
6. | Failure to call nurse | Software or hardware failure | Level 3 Marginal Remote | Manual inspection by personnel Installation of a plan B system | No access to aid/nurse | Level 19 Negligible Remote
7.

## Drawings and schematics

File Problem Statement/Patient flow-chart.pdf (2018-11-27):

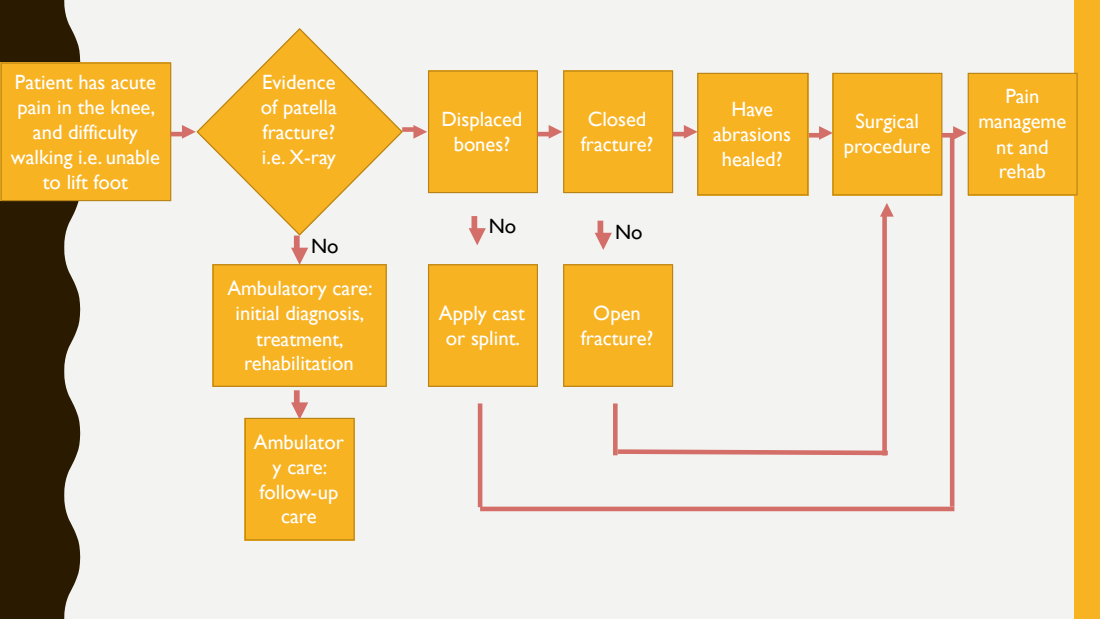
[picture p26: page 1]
Evidence of patella fracture? i.e. X-ray; Ambulatory care: initial diagnosis, treatment, rehabilitation; Ambulator y care: follow-up care; Displaced bones?; Apply cast or splint.; Closed fracture?; Have abrasions healed?; Open fracture?; Surgical procedure; Pain manageme nt and rehab

Patient has acute
pain in the knee,
and difficulty
walking i.e. unable
to lift foot

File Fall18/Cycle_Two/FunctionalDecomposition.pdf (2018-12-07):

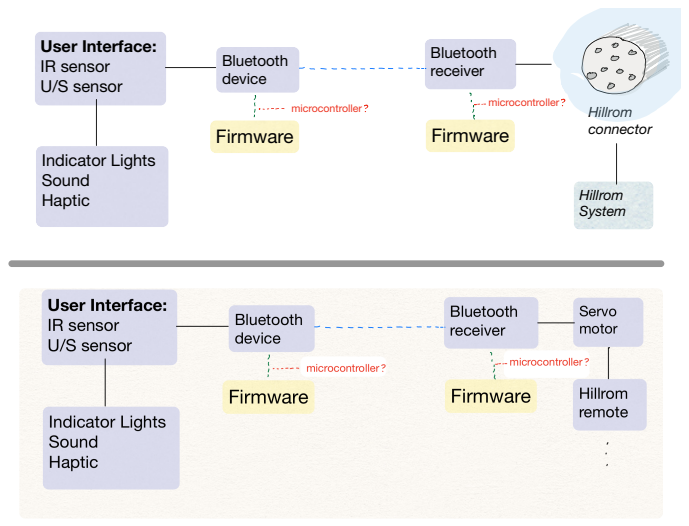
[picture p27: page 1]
l Indicator Lights Sound Haptic; Firmware; microcontroller; User Interface: IR sensor U/S sensor; Bluetooth device; Hillrom connector; Bluetooth receiver; Hillrom System

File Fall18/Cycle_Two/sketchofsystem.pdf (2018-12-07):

i

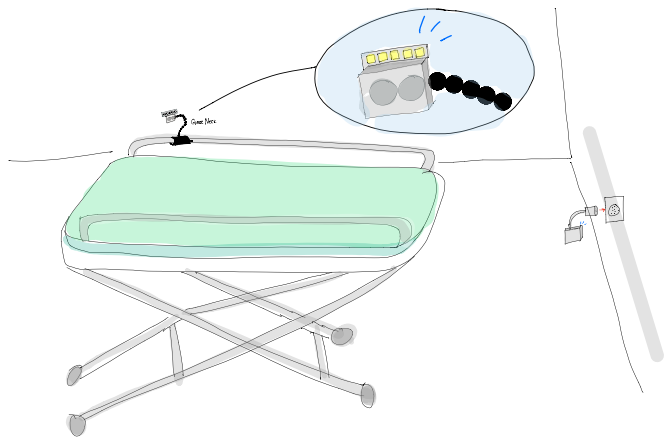
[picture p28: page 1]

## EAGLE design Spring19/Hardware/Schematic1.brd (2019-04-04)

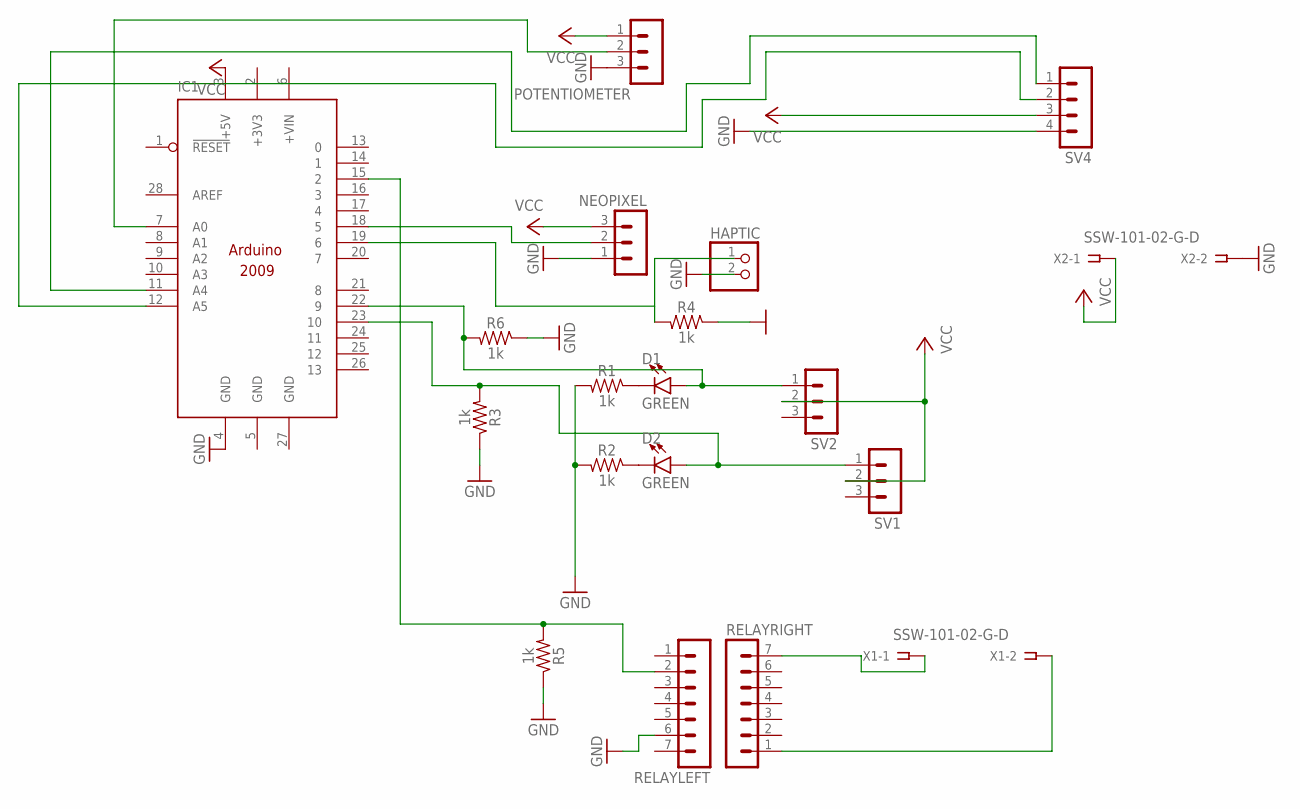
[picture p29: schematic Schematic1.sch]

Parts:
D1, D2: GREEN; LED-1206
HAPTIC: PINHD-1X2; 1X02
IC1: ARDUINO2009_10; ARDUINO2009
NEOPIXEL: MA03-1
POTENTIOMETER: MA03-1
R1, R2, R3, R4, R5, R6: 1k; 0603
RELAYLEFT: MA07-1
RELAYRIGHT: MA07-1
SV1, SV2: MA03-1
SV4: MA04-1
X1, X2: SSW-101-02-G-D

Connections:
+3V3: IC1.2 (+3V3)
GND: HAPTIC.2, IC1.4 (GND), IC1.5 (GND), IC1.27 (GND), NEOPIXEL.1, POTENTIOMETER.3, R1.2, R2.2, R3.1, R4.1, R5.1, R6.1, RELAYLEFT.6, SV4.4, X2.2
unnamed: D1.C, R1.1
unnamed: D2.C, R2.1
unnamed: D2.A, IC1.23 (10), R3.2, SV1.1
unnamed: D1.A, IC1.22 (9), R6.2, SV2.1
unnamed: IC1.18 (5), NEOPIXEL.2
unnamed: IC1.11 (A4), SV4.1
unnamed: IC1.12 (A5), SV4.2
unnamed: HAPTIC.1, IC1.19 (6), R4.2
unnamed: RELAYRIGHT.7, X1.1
unnamed: IC1.7 (A0), POTENTIOMETER.2
unnamed: RELAYRIGHT.1, X1.2
unnamed: IC1.15 (2), R5.2, RELAYLEFT.2
VCC: IC1.3 (+5V), NEOPIXEL.3, POTENTIOMETER.1, SV1.2, SV2.2, SV4.3, X2.1

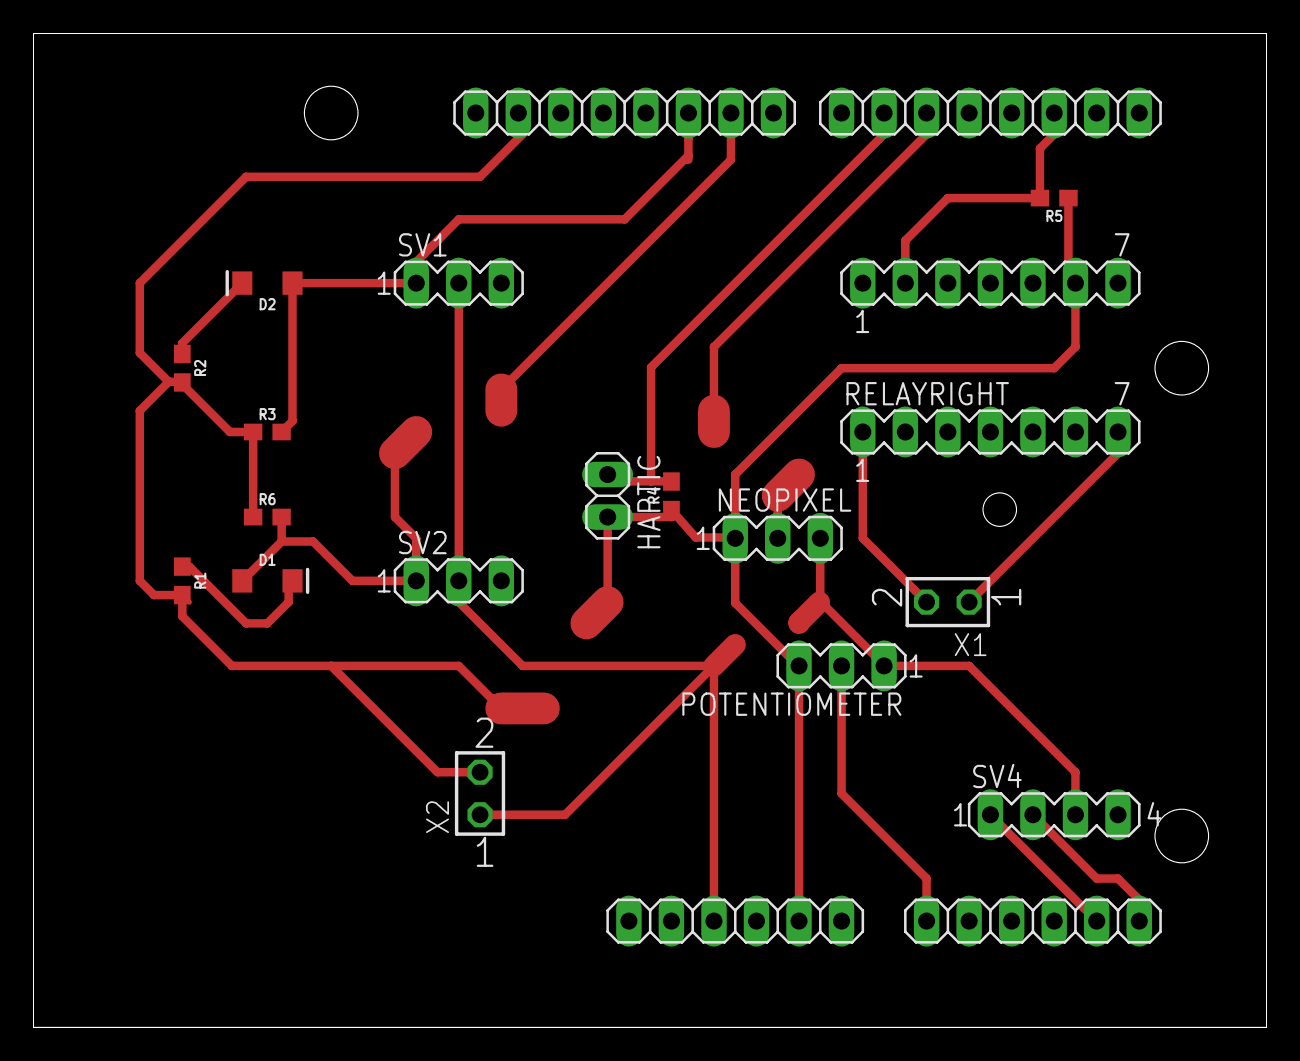
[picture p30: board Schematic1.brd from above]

Board: 2 copper layers, 73.6 x 59.4 mm, 19 parts (0 on the bottom side), 14 nets.

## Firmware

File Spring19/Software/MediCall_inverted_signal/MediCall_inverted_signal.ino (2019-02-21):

#include <Wire.h>
#include <SPI.h>
#include <Adafruit_CAP1188.h>
#define CAP1188_RESET  9
Adafruit_CAP1188 cap = Adafruit_CAP1188();
#include "Adafruit_DRV2605.h"

Adafruit_DRV2605 drv;

int LED1 = 30;
int LED2 = 32;
int LED3 = 34;
int LED4 = 36;
int LED5 = 38;
int signalPin = 52;
int counter = 1;
unsigned long timer = 0;
bool signal_switch = false;
unsigned long signal_lost = 0;
unsigned long read_pot = 0;
float call_delay_float = 0.0000;
int call_delay = 0;
bool LIGHTS = false;
bool HAPTIC = false;
bool SOUND = false;
bool PROX = false;
#define lights_pin 42
#define haptic_pin 44
#define sound_pin 46
#define prox_pin 48
bool switch_status = 0;
#define pot A0
#define haptic_motor 2
int value = 0;
int effect = 19;
// Pot step 0.01265 Seconds

void setup() {
  // put your setup code here, to run once:
  pinMode(LED1, OUTPUT);
  pinMode(LED2, OUTPUT);
  pinMode(LED3, OUTPUT);
  pinMode(LED4, OUTPUT);
  pinMode(LED5, OUTPUT);
  pinMode(signalPin, INPUT);
  pinMode(pot, INPUT);
  pinMode(lights_pin, INPUT);
  pinMode(haptic_pin, INPUT);
  pinMode(sound_pin, INPUT);
  pinMode(prox_pin, INPUT);
  pinMode(haptic_motor, OUTPUT);
  Serial.begin(9600);
  Serial.println("CAP1188 test!");

  // Initialize the sensor, if using i2c you can pass in the i2c address
  // if (!cap.begin(0x28)) {
  if (!cap.begin()) {
    Serial.println("CAP1188 not found");
    while (1);
  }
  Serial.println("CAP1188 found!");
  // HAPTIC
  drv.begin();

  drv.selectLibrary(1);

  // I2C trigger by sending 'go' command
  // default, internal trigger when sending GO command
  drv.setMode(DRV2605_MODE_INTTRIG);
}

void loop() {
  // put your main code here, to run repeatedly:
  check_buttons();
  uint8_t value = cap.touched();
  read_pot = analogRead(pot);
  call_delay_float = read_pot * 0.0127;
  call_delay = call_delay_float * 1000;
  //Serial.println(call_delay);
  while (value) {
    check_buttons();
    if (counter) {
      timer = millis();
      counter = 0;
      //Serial.println(timer);
      //Serial.println(counter);
    }
    if (millis() - timer > call_delay) {
      if (HAPTIC) {
        analogWrite(haptic_motor, 255);
      }
      if (LIGHTS) {
        blink_lights();
        blink_lights();
      }
      if (HAPTIC) {
        analogWrite(haptic_motor, 0);
      }
      signal_lost = 0;
      signal_switch = true;
      Serial.println("Call Placed");
      break;
    }
    if (millis() - timer > call_delay / 5 * 4) {
      if (LIGHTS) {
        digitalWrite(LED5, HIGH);
      }
      vibe();
    }
    else if (millis() - timer > call_delay / 5 * 3) {
      if (LIGHTS) {
        digitalWrite(LED4, HIGH);
      }
      vibe();
    }
    else if (millis() - timer > call_delay / 5 * 2) {
      if (LIGHTS) {
        digitalWrite(LED3, HIGH);
      }
      vibe();
    }
    else if (millis() - timer > call_delay / 5 * 1) {
      if (LIGHTS) {
        digitalWrite(LED2, HIGH);
      }
      vibe();
    }
    else if (millis() - timer > 10) {
      if (LIGHTS) {
        digitalWrite(LED1, HIGH);
      }
      vibe();
    }
    uint8_t value = cap.touched();
    //int value = digitalRead(signalPin);
    if (!value && signal_switch == true) {
      signal_lost = millis();
      signal_switch = false;
    }
    if (value) {
      signal_lost = 0;
      signal_switch = true;
    }
    if (millis() - signal_lost > 500 && signal_switch == false) {
      break;
    }
    //Serial.println(value);
  }
  counter = 1;
  reset_lights();
  value = 0;
}

void reset_lights() {
  digitalWrite(LED1, LOW);
  digitalWrite(LED2, LOW);
  digitalWrite(LED3, LOW);
  digitalWrite(LED4, LOW);
  digitalWrite(LED5, LOW);
}

void lights_on() {
  digitalWrite(LED5, HIGH);
  digitalWrite(LED4, HIGH);
  digitalWrite(LED3, HIGH);
  digitalWrite(LED2, HIGH);
  digitalWrite(LED1, HIGH);
}
void blink_lights() {
  lights_on();
  delay(250);
  reset_lights();
  delay(250);
  lights_on();
  delay(250);
  reset_lights();
  delay(250);
}

void check_buttons() {
  switch_status = digitalRead(lights_pin);
  if (switch_status) {
    LIGHTS = true;
  }
  else {
    LIGHTS = false;
    reset_lights();
  }
  switch_status = digitalRead(haptic_pin);
  if (switch_status) {
    HAPTIC = true;
  }
  else {
    HAPTIC = false;
    analogWrite(haptic_motor, 0);
  }
  switch_status = digitalRead(sound_pin);
  if (switch_status) {
    SOUND = true;
  }
  else {
    SOUND = false;
  }
  switch_status = digitalRead(prox_pin);
  if (switch_status) {
    PROX = true;
  }
  else {
    PROX = false;
  }
}

void vibe() {
  if (HAPTIC) {
    drv.setWaveform(0, effect);  // play effect
    drv.setWaveform(1, 0);       // end waveform

    // play the effect!
    drv.go();
  }
}

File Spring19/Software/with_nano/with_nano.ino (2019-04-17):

#include <Wire.h>
#include <SPI.h>
#include <Adafruit_CAP1188.h>
#define CAP1188_RESET  9
Adafruit_CAP1188 cap = Adafruit_CAP1188();
#include "Adafruit_DRV2605.h"


Adafruit_DRV2605 drv;

#include <Adafruit_NeoPixel.h>
#ifdef __AVR__
#include <avr/power.h>
#endif
#define PIN 5

Adafruit_NeoPixel strip = Adafruit_NeoPixel(60, PIN, NEO_GRB + NEO_KHZ800);

#include "Arduino.h"




int signalPin = 52;
int counter = 1;
unsigned long timer = 0;
bool signal_switch = false;
unsigned long signal_lost = 0;
unsigned long read_pot = 0;
float call_delay_float = 0.0000;
int call_delay = 5000;
int call_delay_temp = 0;
bool LIGHTS = true;
bool HAPTIC = false;
bool SOUND = false;
bool PROX = false;
#define lights_pin 9
#define haptic_pin 10
#define sound_pin 11
#define prox_pin 12
#define PLUG 2
#define nano A4
bool switch_status = 0;
#define pot A0
#define haptic_motor 6
int value = 0;
int effect = 19;
// Pot step 0.01265 Seconds
uint32_t red = strip.Color(255, 0, 0);
uint32_t green = strip.Color(0, 255, 0);
uint32_t blue = strip.Color(0, 0, 255);

void setup() {
  // put your setup code here, to run once:
  pinMode(signalPin, INPUT);
  pinMode(pot, INPUT);
  pinMode(lights_pin, INPUT);
  pinMode(haptic_pin, INPUT);
  pinMode(sound_pin, INPUT);
  pinMode(prox_pin, INPUT);
  pinMode(haptic_motor, OUTPUT);
  pinMode(PLUG, OUTPUT);
  Serial.begin(9600);
  Serial.println("Begin");
  // HAPTIC


  // I2C trigger by sending 'go' command
  // default, internal trigger when sending GO command


  strip.begin();
  strip.setBrightness(50);
  strip.show(); // Initialize all pixels to 'off'

}

void loop() {
  // put your main code here, to run repeatedly:
  check_buttons();
  int value = analogRead(nano);
  if (value < 500){
    value = 0;
  }
  //Serial.println(value);
  float read_pot = analogRead(pot);
  Serial.println(read_pot);
  float call_delay_float = read_pot / 1023;
  call_delay_temp = call_delay_float * 10000;
  if (call_delay_temp){
    call_delay = call_delay_temp;
    Serial.print("Set Delay: ");
    Serial.println(call_delay / 1000);
  }
  //call_delay = 5000;
  while (value) {
    check_buttons();
    if (counter) {
      timer = millis();
      counter = 0;
      //Serial.println(timer);
      //Serial.println(counter);
    }
    if (millis() - timer > call_delay) {
      digitalWrite(PLUG, HIGH);
      if (HAPTIC) {
        analogWrite(haptic_motor, 255);
      }
      if (LIGHTS) {
        blinkLights();
        blinkLights();
        blinkLights();
      }
      analogWrite(haptic_motor, 0);
      signal_lost = 0;
      signal_switch = true;
      Serial.println("Call Placed");
      digitalWrite(PLUG, LOW);
      break;
    }
    if (millis() - timer > call_delay / 5 * 4) {
      if (LIGHTS) {
        colorUpdate(red, 5);
        colorUpdate(red, 1);
        colorUpdate(red, 2);
        colorUpdate(red, 3);
        colorUpdate(red, 4);
      }
      vibe();
    }
    else if (millis() - timer > call_delay / 5 * 3) {
      if (LIGHTS) {
        colorUpdate(red, 4);
        colorUpdate(red, 1);
        colorUpdate(red, 2);
        colorUpdate(red, 3);
      }
      vibe();

    }
    else if (millis() - timer > call_delay / 5 * 2) {
      if (LIGHTS) {
        colorUpdate(red, 3);
        colorUpdate(red, 1);
        colorUpdate(red, 2);
      }
      vibe();

    }
    else if (millis() - timer > call_delay / 5 * 1) {
      if (LIGHTS) {
        colorUpdate(red, 1);
        colorUpdate(red, 2);
      }
      vibe();
    }
    else if (millis() - timer > 10) {
      if (LIGHTS) {
        colorUpdate(red, 1);
      }
      vibe();
      //delay(100000);
    }
int value = analogRead(nano);
  if (value < 500){
    value = 0;
  }
    //Serial.println(value);
    if (!value && signal_switch == true) {
      signal_lost = millis();
      signal_switch = false;
    }
    if (value) {
      signal_lost = 0;
      signal_switch = true;
    }
    if (millis() - signal_lost > 500 && signal_switch == false) {
      break;
    }
    //Serial.println(value);
  }
  counter = 1;
  value = 0;
  for (uint16_t i = 0; i < strip.numPixels(); i++) {
    strip.setPixelColor(i, 0);
    strip.show();
  }
}

void check_buttons() {
  switch_status = digitalRead(lights_pin);
  if (switch_status) {
    LIGHTS = true;
  }
  else {
    LIGHTS = false;
    for (uint16_t i = 0; i < strip.numPixels(); i++) {
      strip.setPixelColor(i, 0);
      strip.show();
    }
  }
  switch_status = digitalRead(haptic_pin);
  if (switch_status) {
    HAPTIC = true;
  }
  else {
    HAPTIC = false;
    analogWrite(haptic_motor, 0);
  }
}

void vibe() {
  if (HAPTIC) {
    analogWrite(haptic_motor, 75);
    delay(50);
    analogWrite(haptic_motor, 0);
  }
}

void colorUpdate(uint32_t c, int pixel) {
  strip.setPixelColor(pixel, c);
  strip.show();
}

void blinkLights() {
  for (uint16_t i = 0; i < strip.numPixels(); i++) {
    strip.setPixelColor(i, green);
    strip.show();
  }
  delay(500);
  for (uint16_t i = 0; i < strip.numPixels(); i++) {
    strip.setPixelColor(i, 0);
    strip.show();
  }
}

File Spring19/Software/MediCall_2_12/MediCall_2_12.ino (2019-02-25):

#include <Wire.h>
#include <SPI.h>
#include <Adafruit_CAP1188.h>
#define CAP1188_RESET  9
Adafruit_CAP1188 cap = Adafruit_CAP1188();
#include "Adafruit_DRV2605.h"
/* This is packages necessary for DFPlayer
  #include "Arduino.h"
  #include "SoftwareSerial.h"
  #include "DFRobotDFPlayerMini.h"
*/

Adafruit_DRV2605 drv;

SoftwareSerial mySoftwareSerial(7, 8); // DF pin 2 goes to 11, DF pin 3 goes to 10
DFRobotDFPlayerMini myDFPlayer;
void printDetail(uint8_t type, int value);


#include <Adafruit_NeoPixel.h>
#ifdef __AVR__
#include <avr/power.h>
#endif
#define PIN 5

Adafruit_NeoPixel strip = Adafruit_NeoPixel(60, PIN, NEO_GRB + NEO_KHZ800);
int counter = 1;
unsigned long timer = 0;
bool signal_switch = false;
unsigned long signal_lost = 0;
unsigned long read_pot = 0;
float call_delay_float = 0.0000;
int call_delay = 0;
bool LIGHTS = true;
bool HAPTIC = false;
bool SOUND = false;
bool PROX = false;
#define lights_pin 6
#define haptic_pin 7
#define sound_pin 8
#define prox_pin 9
bool switch_status = 0;
#define pot A0
#define haptic_motor 3
int value = 0;
int effect = 19;
// Pot step 0.01265 Seconds
uint32_t red = strip.Color(255, 0, 0);
uint32_t green = strip.Color(0, 255, 0);
uint32_t blue = strip.Color(0, 0, 255);

void setup() {
  // put your setup code here, to run once:
  pinMode(pot, INPUT);
  pinMode(lights_pin, INPUT);
  pinMode(haptic_pin, INPUT);
  pinMode(sound_pin, INPUT);
  pinMode(prox_pin, INPUT);
  pinMode(haptic_motor, OUTPUT);
  Serial.begin(115200);
  Serial.println("CAP1188 test!");

  // Initialize the sensor, if using i2c you can pass in the i2c address
  // if (!cap.begin(0x28)) {
  if (!cap.begin()) {
    Serial.println("CAP1188 not found");
    while (1);
  }
  Serial.println("CAP1188 found!");
  // HAPTIC
  drv.begin();

  drv.selectLibrary(1);

  // I2C trigger by sending 'go' command
  // default, internal trigger when sending GO command
  drv.setMode(DRV2605_MODE_INTTRIG);

  strip.begin();
  strip.setBrightness(50);
  strip.show(); // Initialize all pixels to 'off'

  // This is the set up code from DFPlayer_test
  mySoftwareSerial.begin(9600);

  Serial.println();
  Serial.println(F("DFRobot DFPlayer Mini Demo"));
  Serial.println(F("Initializing DFPlayer ... (May take 3~5 seconds)"));

  if (!myDFPlayer.begin(mySoftwareSerial)) {  //Use softwareSerial to communicate with mp3.
    Serial.println(F("Unable to begin:"));
    Serial.println(F("1.Please recheck the connection!"));
    Serial.println(F("2.Please insert the SD card!"));
    while (true);
  }
  Serial.println(F("DFPlayer Mini online."));

  myDFPlayer.volume(30);  //Set volume value. From 0 to 30

}

void loop() {
  // put your main code here, to run repeatedly:
  check_buttons();
  uint8_t value = cap.touched();
  read_pot = analogRead(pot);
  call_delay_float = read_pot * 0.0127;
  call_delay = call_delay_float * 1000;
  while (value) {
    check_buttons();
    if (counter) {
      timer = millis();
      counter = 0;
      //Serial.println(timer);
      //Serial.println(counter);
    }
    if (millis() - timer > call_delay) {
      if (HAPTIC) {
        analogWrite(haptic_motor, 255);
      }
      if (LIGHTS) {
        blinkLights();
        blinkLights();
        blinkLights();
      }
      analogWrite(haptic_motor, 0);
      signal_lost = 0;
      signal_switch = true;
      Serial.println("Call Placed");
      break;
    }
    if (millis() - timer > call_delay / 5 * 4) {
      if (LIGHTS) {
        colorUpdate(red, 4);
      }
      vibe();
      load_sound();
    }
    else if (millis() - timer > call_delay / 5 * 3) {
      if (LIGHTS) {
        colorUpdate(red, 3);
      }
      vibe();

    }
    else if (millis() - timer > call_delay / 5 * 2) {
      if (LIGHTS) {
        colorUpdate(red, 2);
      }
      vibe();
    }
    else if (millis() - timer > call_delay / 5 * 1) {
      if (LIGHTS) {
        colorUpdate(red, 1);
      }
      vibe();
      load_sound();
    }
    else if (millis() - timer > 10) {
      Serial.print("LIGHTS:");
      Serial.println(LIGHTS);
      if (LIGHTS) {
        colorUpdate(strip.Color(255, 0, 0), 0);
      }
      vibe();
      //delay(100000);
    }
    uint8_t value = cap.touched();
    if (!value && signal_switch == true) {
      signal_lost = millis();
      signal_switch = false;
    }
    if (value) {
      signal_lost = 0;
      signal_switch = true;
    }
    if (millis() - signal_lost > 500 && signal_switch == false) {
      break;
    }
    //Serial.println(value);
  }
  counter = 1;
  value = 0;
  for (uint16_t i = 0; i < strip.numPixels(); i++) {
    strip.setPixelColor(i, 0);
    strip.show();
  }
  /* This is the loop code for the DFPlayer.
    static unsigned long timer = millis();

    if (millis() - timer > 3000) {
    timer = millis();
    myDFPlayer.next();  //Play next mp3 every 3 second.
    }

    if (myDFPlayer.available()) {
    printDetail(myDFPlayer.readType(), myDFPlayer.read()); //Print the detail message from DFPlayer to handle different errors and states.
    }
  */
}
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

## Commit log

2018-11-27 Add all documents from google drive
    [HaerynLizDeepthi_Medical Device Development Worksheet 2018.xlsx, Medical Device Development Worksheet 2018.xlsx]
2018-11-28 Initial CAD designs
    [clamp.SLDPRT, sensor holder.SLDPRT, sensor.SLDPRT, strokesensorassembly.SLDASM]
2018-12-01 Pugh Matrices
    [BatteryvsMains.xlsx, Scoring_Alert.xlsx, Scoring_Sensor.xlsx, Scoring_User_Alert.xlsx]
2018-12-02 Add testing plan
    [HaerynLizDeepthi_Medical Device Development Worksheet 2018.xlsx]
2018-12-02 Adjust cell widths
    [HaerynLizDeepthi_Medical Device Development Worksheet 2018.xlsx]
2018-12-03 Add Device Powering Mechanism Pugh Matrix in addition to pro-con list
    [Scoring_Battery.xlsx]
2018-12-05 Add to final presentation
    [HaerynLizDeepthi_Medical Device Development Worksheet 2018.xlsx]
2018-12-07 Add rechargeable battery options
    [Scoring_Battery.xlsx]
2018-12-07 Add sketch and functional decomposition of device
2018-12-07 Add excel sheet pdf
    [HaerynLizDeepthi_Medical Device Development Worksheet 2018.xlsx, single_sheet_HOQ_Specs.xlsx]
2018-12-07 adjust specs
    [HOQ Spec.xlsx, single_sheet_HOQ_Specs.xlsx]
2018-12-07 Save submitted HOQ
    [HOQ and Specs SUBMISSION.xlsx]
2018-12-07 Add pdf of updated objectives
    [HOQ and Specs SUBMISSION.xlsx, HaerynLizDeepthi_Medical Device Development Worksheet 2018.xlsx]
2018-12-07 Add directory of current repository
2018-12-07 Add old slide with three parts of prototype
    [HaerynLizDeepthi_Medical Device Development Worksheet 2018.xlsx]
2019-01-25 Add Arduino code that connects IR sensor to LEDs
2019-02-25 Working EAGLE schematic
    [Schematic1.sch]
2019-03-11 Updated schematic with arduino shield
    [Schematic1.brd]
2019-03-12 Attempt 1 at routing
    [Schematic1.sch]
2019-03-18 Finish routing
    [Schematic1.sch]
2019-03-18 Add through holes for plug
    [Schematic1.brd, Schematic1.sch]
2019-03-19 Single sided board with airwires
    [Schematic1.brd]
2019-03-19 Fix relay width
    [Schematic1.brd, Schematic1.sch]
2019-03-19 Adjst trace widths
    [Schematic1.brd]
2019-03-19 Adjust wonky routes
    [Schematic1.brd]
2019-03-20 Adjust cap1188 footprint and add some bottom routes
    [Schematic1.brd, Schematic1.sch]
2019-03-20 Adjust routes
    [Schematic1.brd]
2019-03-20 airwire route thickness
    [Schematic1.brd]
2019-03-20 Switch back to airwires; single sided boards
    [Schematic1.brd]
2019-03-20 adjust routes again
    [Schematic1.brd]
2019-03-27 PCB for etching
    [Schematic1.brd, Schematic1.sch]
2019-03-28 Switch relay direction
    [Schematic1.brd, Schematic1.sch]
2019-04-04 for etching 4.3.19
    [Schematic1.brd, Schematic1.sch]
2019-04-14 Add hazard analysis report
    [BatteryvsMains.xlsx, HOQ Spec.xlsx, HOQ and Specs SUBMISSION.xlsx, HaerynLizDeepthi_Medical Device Development Worksheet 2018.xlsx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]
2019-04-17 Add Parts List
    [Parts List.xlsx]
2019-04-17 Update with total cost
    [Parts List.xlsx]
2019-04-17 Add Semester Parts List
    [Parts List Semester.xlsx]
2019-04-18 Add files via upload
    TO PRINT
    [Cut-Extrude10.sldprt]
2019-04-22 add power supply hole
    [001_sensor_bottom.SLDPRT, 002_sensor_top.SLDPRT, 004_box_top.STL, Cut-Extrude10.sldprt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]
2019-04-22 Add files via upload
    Adjust hole size for threaded inserts
    [002_sensor_top.SLDPRT, 004_box_top.STL]
2019-04-22 Add files via upload
    sensor top changes
    [002_sensor_top.SLDPRT, 002_sensor_top.STL]
2019-04-25 Add pdfs of drawings
    [001_sensor_bottom_drawing.SLDDRW, 002_sensor_top_drawing.SLDDRW, 003_box_bottom_drawing.SLDDRW, 004_box_top_drawing.SLDDRW]
2019-04-30 Add customer satisfaction survey
    Necessary device evaluation component
2019-05-03 Add editable CAD files etc in Appendix E
    [001_sensor_bottom.SLDPRT, 001_sensor_bottom_drawing.SLDDRW, 002_sensor_top.SLDPRT, 002_sensor_top.STL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]

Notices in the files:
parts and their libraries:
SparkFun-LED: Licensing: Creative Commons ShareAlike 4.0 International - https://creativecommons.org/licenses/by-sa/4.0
